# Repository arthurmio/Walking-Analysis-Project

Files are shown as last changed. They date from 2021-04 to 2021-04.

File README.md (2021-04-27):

# Walking-Analysis-Project
Projet d'analyse de la marche réalisé par :
  - GOURDON Mathéo
  - MARIANO Arthur 
  - TRIGUI Ianis

Ce projet a été développé dans le cadre du projet "Fil Rouge" en 5ème année à l'ESIEE Paris.  
Ce prototype d'analyse propose une solution d'analyse de la marche sans fil à l'aide d'Arduinos 33 BLE et de capteurs inertiels (BNO005) connectées grâce au protocole BLE (Bluetooth Low Energy). La lecture et l'interprétation des données sont réalisées à l'aide d'une interface sous Python.

# How to use it
Afin d'utiliser correctement le prototype veuillez vous référer à la notice d'utilisation dans le répertoire "Documentation".

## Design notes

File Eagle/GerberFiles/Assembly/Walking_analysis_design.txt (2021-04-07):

Partlist exported from C:/Users/Mathéo/Desktop/ESIEE/E5FE/projet_marche/Walking_analysis_design.sch at 14/03/2021 18:37

Qty Value               Device               Package              Parts Description                                      DESCRIPTION                                      HEIGHT MANUFACTURER_NAME MANUFACTURER_PART_NUMBER POPULARITY PROD_ID    RS_PART_NUMBER RS_PRICE-STOCK                                  VALUE
1                       RESISTORAXIAL-0.3    AXIAL-0.3            R1    Generic Resistor Package                                                                                                                                                                                                                      
1   0.1uF               0.1UF-KIT-EZ-50V-20% CAP-PTH-SMALL-KIT    C1    0.1µF ceramic capacitors                                                                                                                                       CAP-08370                                                                 0.1uF
1   5MS3S402AM2QES      5MS3S402AM2QES       5MS3S402AM2QES       S1    PCB Slide Switch SPDT On-Off-On 5 A@ 28 V dc Top PCB Slide Switch SPDT On-Off-On 5 A@ 28 V dc Top 9.91mm RS Components     5MS3S402AM2QES                                 7347334        https://uk.rs-online.com/web/p/products/7347334      
1   ARDUINO-NANO-3.0    ARDUINO-NANO-3.0     ARDUINO-NANO-3.0     M1    Arduino Nano 3.0 and compatible devices                                                                                                                                                                                                       
1   BNO055              BNO055               BNO055_FOOTPRINT     U$1   BNO055_walking analysis                                                                                                                                                                                                                       
1   POWER_JACKPTH_BREAD POWER_JACKPTH_BREAD  POWER_JACK_PTH_BREAD J1    Power Jack Connector                                                                                                                                           COMP-13253                                                                     
1   SFH482              SFH482               SFH482               D1    IR LED                                                                                                                                              0

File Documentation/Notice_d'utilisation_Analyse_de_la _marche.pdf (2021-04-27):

# Notice d’utilisation Prototype d’analyse de la marche sans fil

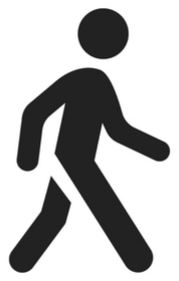
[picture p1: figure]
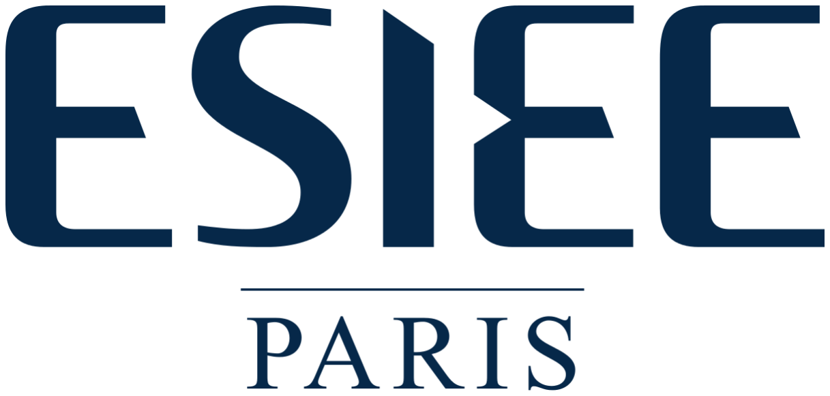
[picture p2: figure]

GOURDON Mathéo
MARIANO Arthur
TRIGUI Ianis

E5FE
2020 - 2021

# Table des matières

Introduction | 3
Matériel nécessaire | 3
Comment utiliser le dispositif | 4
Téléversement des programmes Arduino | 5
Utilisation de l’interface Python | 6

# Introduction

Ce document a pour objectif d’être une notice d’utilisation du projet Analyse de la marche réalisé dans le cadre du projet fil rouge à l’ESIEE Paris. Tous les fichiers nécessaires sont disponibles sur notre github (https://github.com/arthurmio/Walking-Analysis-Project).

Notre document est séparé en deux grandes parties :
- Hardware : consistant en le matériel nécessaire et comment l’utiliser
- Software : consistant à téléverser les programmes Arduino et à utiliser l’interface Python

Pour toutes questions liées à l’utilisation ou à la compréhension de certains fichiers, n’hésitez pas à contacter un des contributeurs du github.

# Matériel nécessaire

Pour se servir de notre dispositif, il est essentiel de se munir de tout le matériel nécessaire. Pour ce qui est du dispositif en lui-même il nous faudra donc les éléments suivant:
- 7 boîtiers;
- 7 batteries chargées 9V;
- 7 circuits imprimés;
- Un ordinateur;
- Un câble micro-usb -> USB.

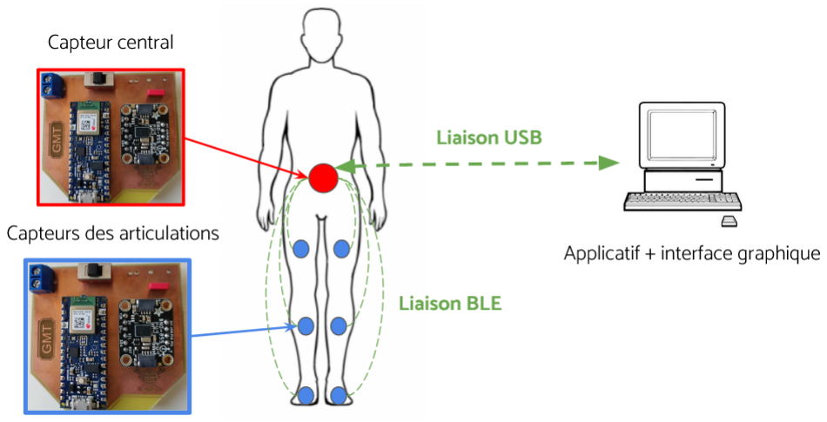
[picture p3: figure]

# Comment utiliser le dispositif

Pour installer le matériel il faut tout d’abord passer les languettes de scratch dans les boîtiers grâce à la fente prévue à cet effet. Puis brancher les batteries aux cartes imprimées de cette manière :

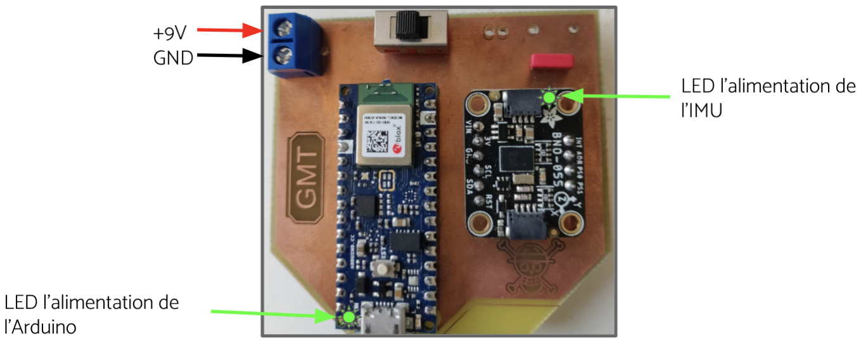
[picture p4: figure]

Si le système est correctement alimenté, alors les LEDs d’alimentation vertes seront allumées sur l’Arduino ainsi que sur le BNO055

Une fois chaque carte alimentée, il faut insérer les batteries dans le boîtier à l’intérieur des encoches afin de les maintenir. Une fois les batteries placées, nous pouvons ajouter le circuit imprimé dans le boîtier et le fermer. La carte reliée au dos doit être reliée grâce au câble micro-usb à un ordinateur portable.

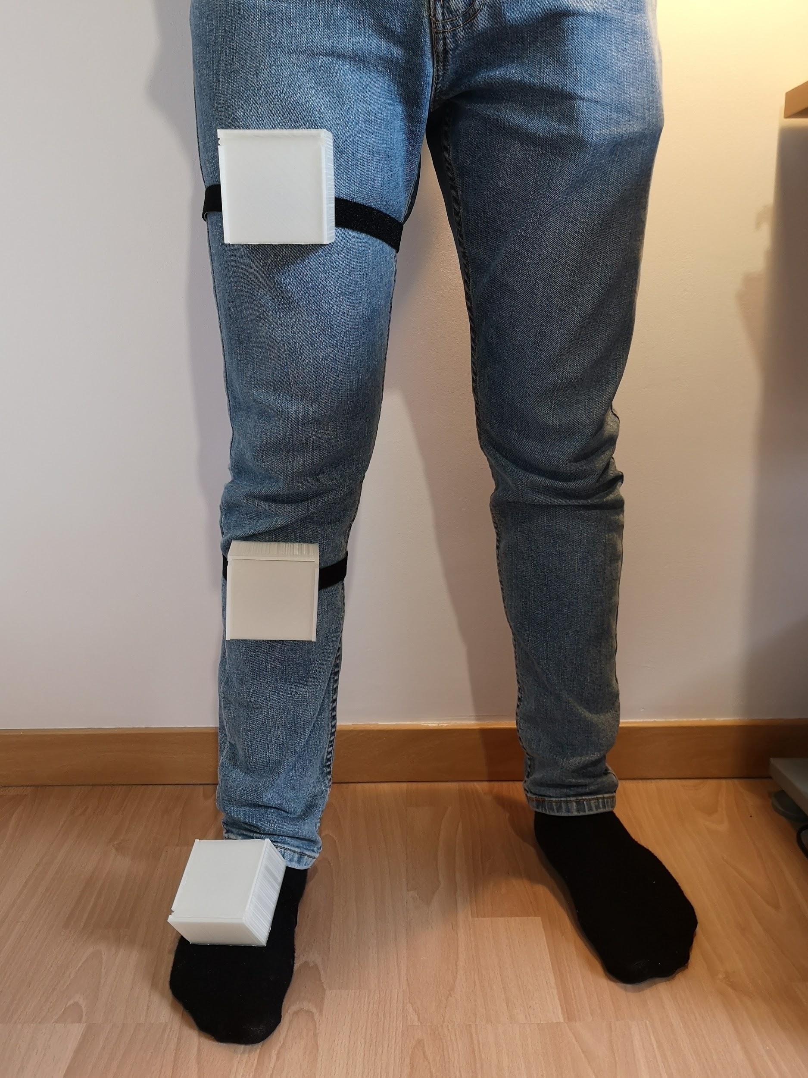
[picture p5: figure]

Pour mettre le circuit en route il suffit d’activer les interrupteurs de chaque carte.

# Téléversement des programmes Arduino

Le logiciel de développement utilisé pour les programmes des cartes Arduino est l’IDE Arduino. Il faudra donc tout d'abord installer l’environnement, pour installer les drivers et les librairies qui seront utilisés pour communiquer avec l’Arduino Nano 33 BLE ainsi qu’avec l’IMU BNO055.

Puis il faudra téléverser les programmes sur l’ensemble des cartes arduino.
Commençons par les 6 capteurs périphériques, les programmes sont situés dans l’arborescence suivante dans le Github : Walking-Analysis-Project/Arduino/Peripherals Chacunes des 6 Arduinos périphériques devront être téléversées avec un programme différent peu importe l’ordre. Les programmes sont notés Peripheral_X.ino avec X allant de 1 à 6. Une fois cette étape réalisée, les périphériques sont désormais initialisés.

Passons maintenant à la centrale, le programme se situe dans l’arborescence suivante : Walking-Analysis-Project/Arduino/Central et le programme se nomme Central.ino, il suffit de le téléverser sur la carte centrale.

Lorsque toutes les cartes auront reçu leur programme maintenant il faut réaliser une calibration rapide des IMUs, pour cela il suffit simplement de tenir dans sa main la capteur et de l’orienter dans toutes les directions.

Une fois toutes les étapes précédentes réalisées, le système est prêt à l’emploi. Afin de notifier si un périphérique se connecte à la centrale, il suffit de regarder si la LED orange est allumée ou non. Si le système fonctionne bien, la centrale devrait se connecter puis se déconnecter à l’ensemble des périphériques. A noter qu’une connexion dure moins d’une seconde.

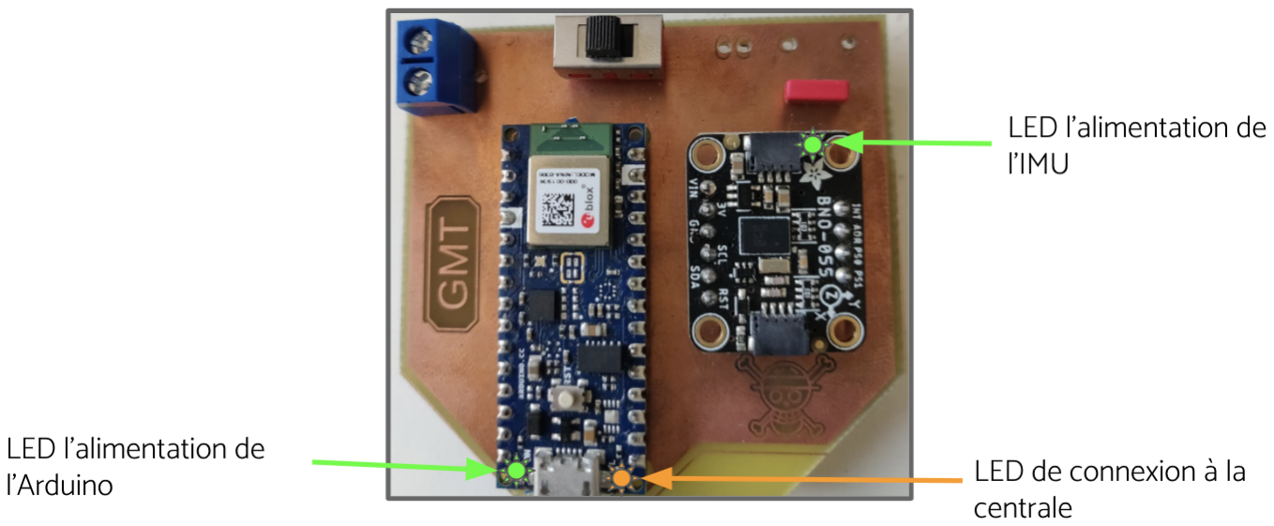
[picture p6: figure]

Si jamais le système cesse de fonctionner, il suffit de re-téléverser le code de la centrale ou bien de “reset” les périphériques bloqués en connexion en appuyant 2 fois sur le bouton reset de l’Arduino concernée.

# Utilisation de l’interface Python

Notre interface à été réalisé sur Python (version 3.9.2). L’IDE de développement a été Visual Studio Code mais ce n’est absolument pas une nécessité de l’utiliser pour faire fonctionner ces programmes.

Cette interface utilise différentes librairies qui devront être téléchargés pour pouvoir exécuter le programme (voir en-tête de chaque programme) :
- numpy;
- matplotlib;
- time;
- serial;
- tkinter.

Les fichiers d’interface sont situés dans le répertoire “python” du github.
Il existe 4 fichiers différents avec chacune une particularité (décrite dans l’en-tête en commentaire) :
- interface.py : est un fichier d’interface (de l’arduino) réalisé avec tkinter permettant de lisser les courbes (peut poser problème);
- interface_bis.py : est le même fichier que interface.py, cependant sans le lissage des courbes (à utiliser principalement);
- serie.py : qui est notre interface avec un affichage des courbes en temps réel (fonctionne moyennement car beaucoup de données sont compliquées à être affichées);
- data_save.py : affiche les différentes courbes de l’arduino, cependant sans l’interface créée avec tkinter.

Avant l’exécution d’un de ces 4 programmes, il faut préciser sur quel port COM est connectée notre arduino centrale.
Pour paramétrer le port COM que nous utilisons dans le programme, il faut modifier la ligne suivante : arduinoData=serial.Serial('COM4', 115200).

Une fois les librairies et les fichiers téléchargés, le port COM paramétré, vous pouvez exécuter un des 4 fichiers en utilisant python3.

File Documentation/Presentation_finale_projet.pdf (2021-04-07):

Projet fil rouge
Présentation finale projet Mme Abir Rezgui

# Analyse de la marche

Mathéo Gourdon
Arthur Mariano
Ianis Trigui

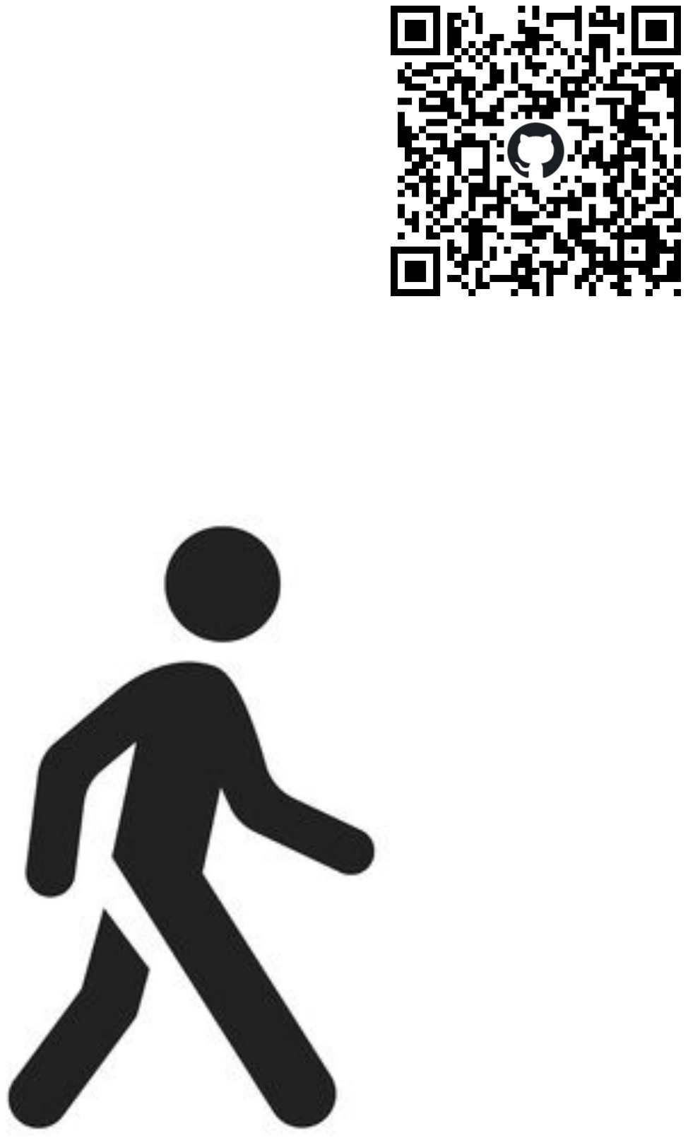
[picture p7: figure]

06/04/2021 | 1

## matières

## Table des

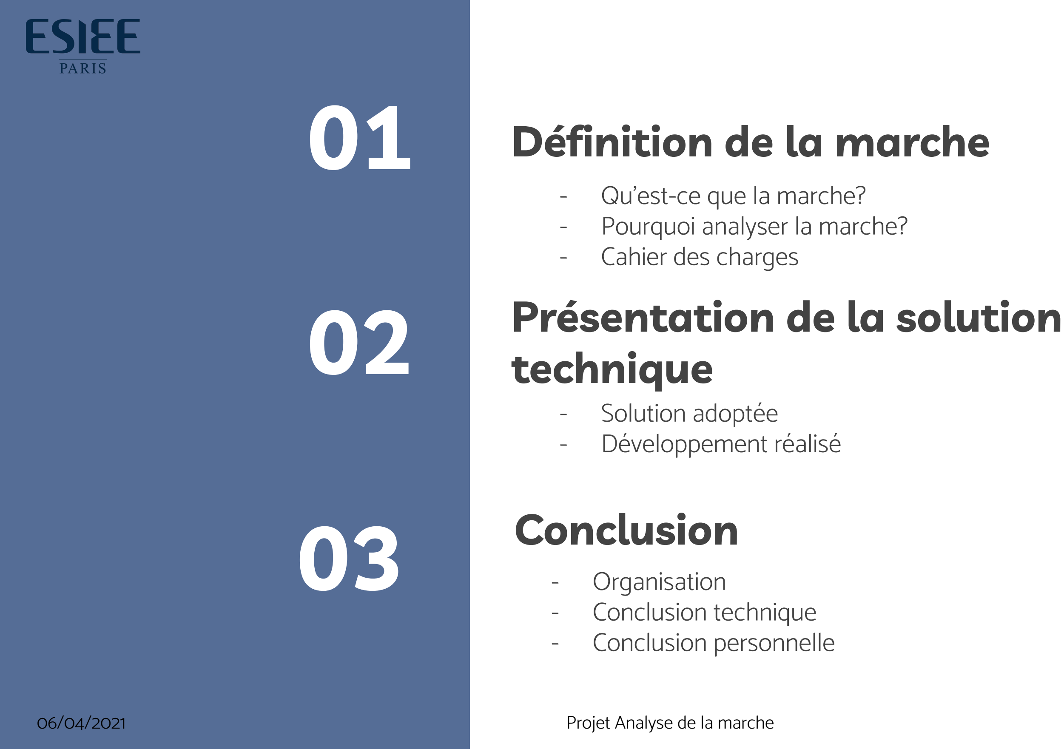
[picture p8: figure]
Conclusion 03; 01 Définition de la marche; Présentation de la solution; Projet Analyse de la marche

technique - Solution adoptée - Développement réalisé

- Qu’est-ce que la marche? - Pourquoi analyser la marche? - Cahier des charges
- Organisation - Conclusion technique - Conclusion personnelle

Projet Analyse de la marche

# 01 - Introduction

## a) Qu’est-ce que la marche?

## b) Pourquoi analyser la marche?

## c) Cahier des charges

06/04/2021 | 3

## Définition de la marche

Projet Analyse de la marche | 4

La marche peut être définie comme un déplacement consistant en une translation de l’ensemble du corps, consécutive à des mouvements de rotations articulaires.

Elle utilise une répétition de séquences des segments corporels pour déplacer le corps vers l’avant en maintenant l’équilibre.

Bouisset et Maton, 1995

Perry, 1992

06/04/2021

## Définition de la marche

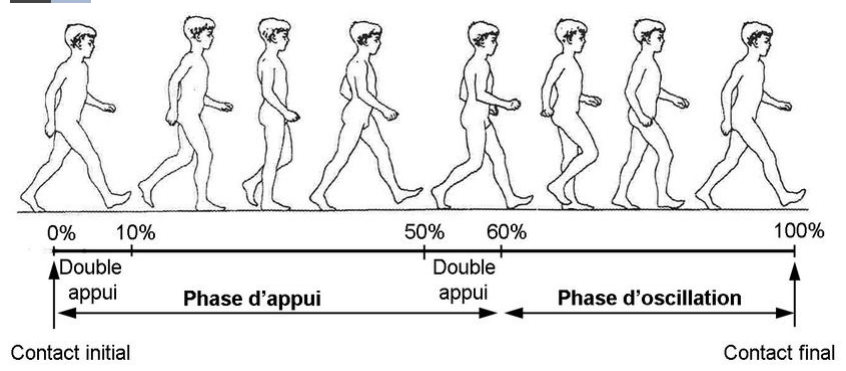
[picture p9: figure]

06/04/2021 | Projet Analyse de la marche | 5

Projet Analyse de la marche

# 01 - Introduction

## a) Qu’est-ce que la marche?

## b) Pourquoi analyser la marche?

## c) Cahier des charges

06/04/2021 | 6

## Pourquoi analyser la marche ?

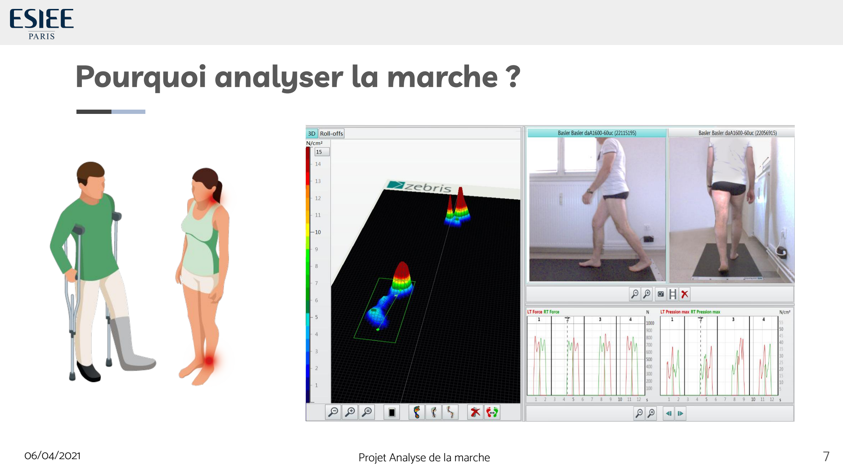
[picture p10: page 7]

06/04/2021 | Projet Analyse de la marche | 7

Projet Analyse de la marche

# 01 - Introduction

## a) Qu’est-ce que la marche?

## b) Pourquoi analyser la marche?

## c) Cahier des charges

06/04/2021 | 8

## Cahier des charges

06/04/2021 | Projet Analyse de la marche

Objectif du projet : Proposer une solution d’analyse de la marche sans fil à moindre coût
Besoins :
- Interconnexion de capteurs en Bluetooth et lire les données avec une fréquence d’acquisition de 100 Hz
- Réaliser une interface graphique permettant de lire les données reçues des différents capteurs
- Réaliser des PCB + un boîtier en modèle 3D pour rendre le dispositif utilisable

Projet Analyse de la marche

# 02 - Présentation de la solution technique

## a) Solution adoptée

## b) Développement réalisé

1) PCB + Impression 3D
2) Arduino
3) Interface Python
06/04/2021 | 10

## Schéma de connectivité de notre système

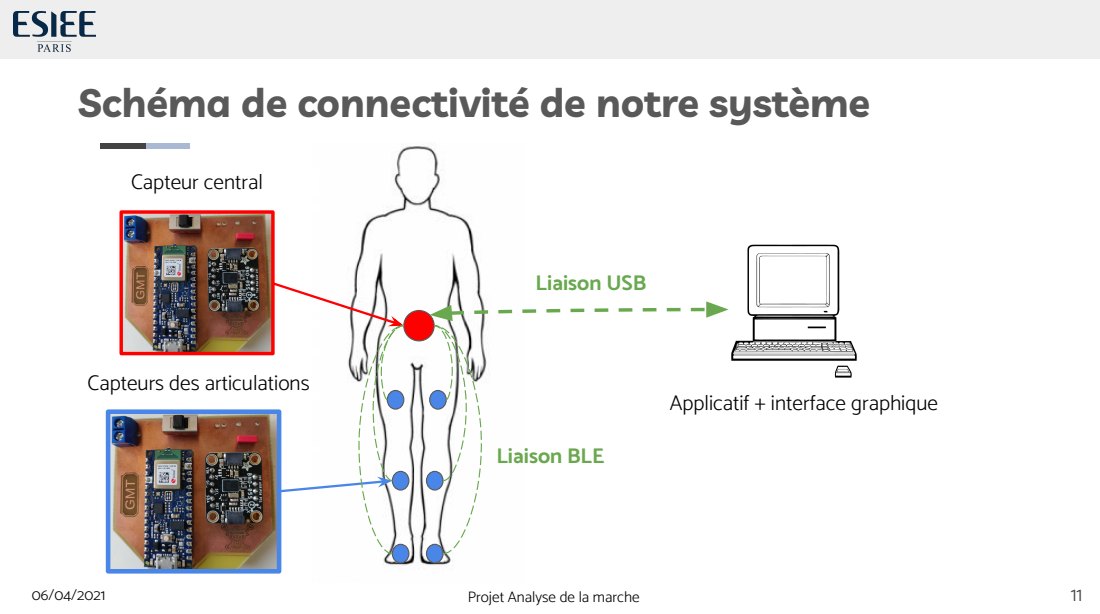
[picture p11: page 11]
Projet Analyse de la marche; Liaison BLE; Liaison USB; Capteur central

Capteurs des articulations

Applicatif + interface graphique

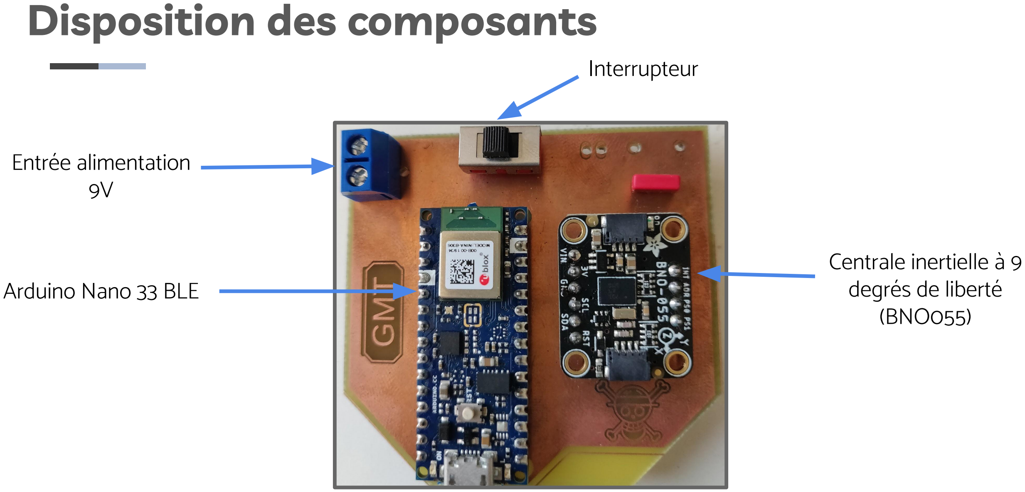
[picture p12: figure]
Disposition des composants; Entrée alimentation 9V; Interrupteur; Centrale inertielle à 9 degrés de liberté (BNO055); Arduino Nano 33 BLE

Projet Analyse de la marche

06/04/2021 | 12

Projet Analyse de la marche

# 02 - Présentation de la solution technique

06/04/2021 | 13

## a) Solution proposée

## b) Développement réalisé

1) PCB + Impression 3D
2) Arduino
3) Interface Python

## Réalisation du PCB

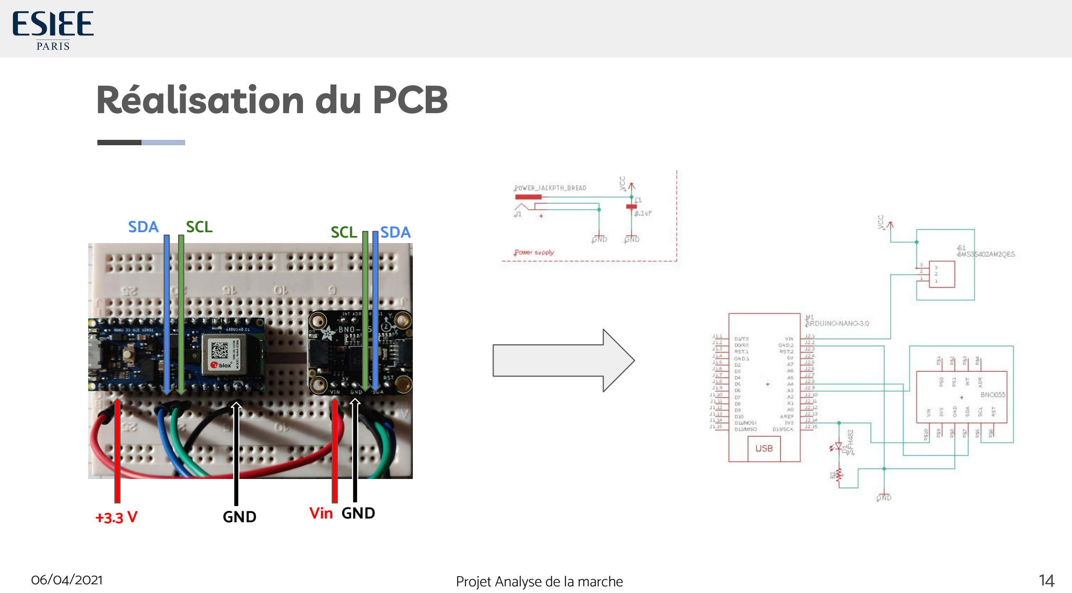
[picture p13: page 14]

SDA | | SCL
SCL | SDA
+3.3 V | GND | Vin GND
06/04/2021 | Projet Analyse de la marche | 14

## Réalisation du PCB

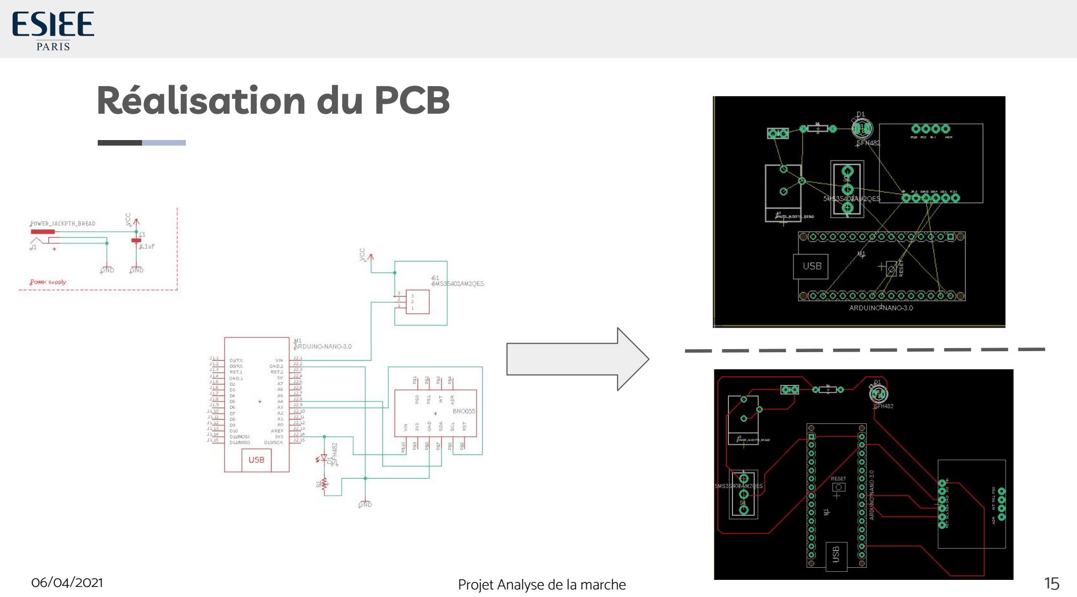
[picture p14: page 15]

06/04/2021 | Projet Analyse de la marche

## Réalisation du PCB

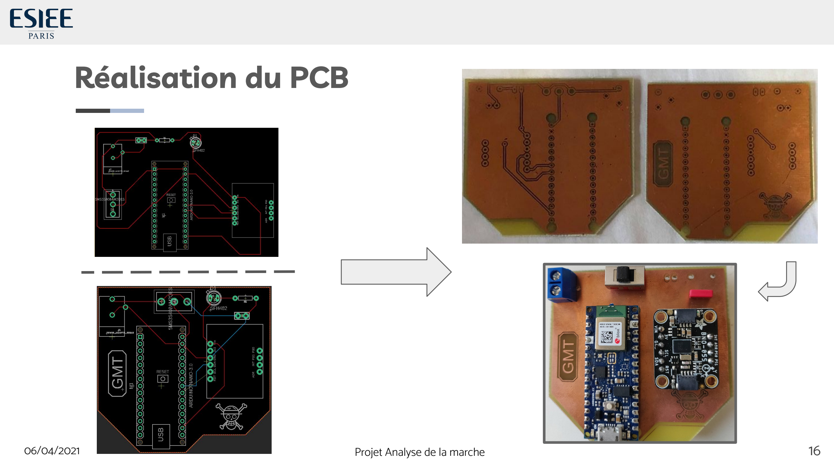
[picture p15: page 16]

06/04/2021 | Projet Analyse de la marche

## Conception du boîtier

- Mesure des dimensions des
différents composants
- Croquis du boîtier
- Création du modèle sur
SketchUp

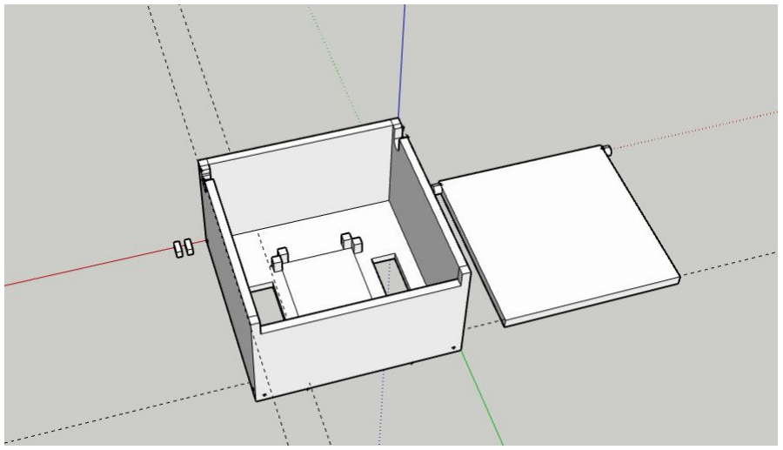
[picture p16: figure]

06/04/2021 | Projet Analyse de la marche | 17

## Conception du boîtier

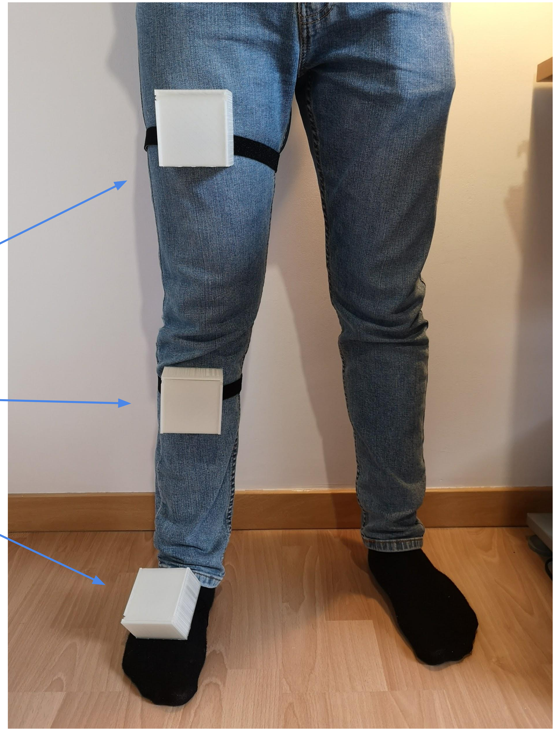
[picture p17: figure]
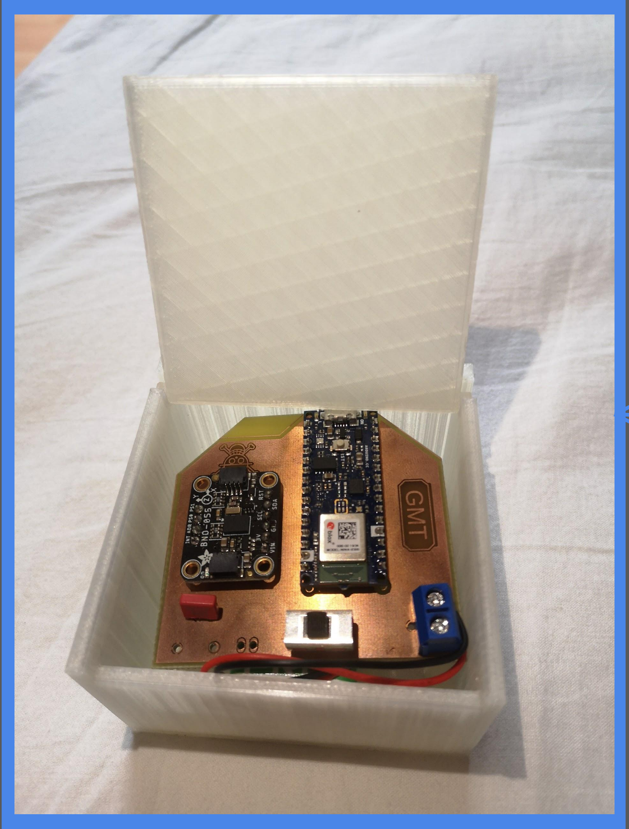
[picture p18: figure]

06/04/2021 | Projet Analyse de la marche

Projet Analyse de la marche

# 02 - Présentation de la solution technique

06/04/2021 | 19

## a) Solution adoptée

## b) Développement réalisé

1) PCB + Impression 3D
2) Arduino
3) Interface Python

## Travail réalisé sur les segments

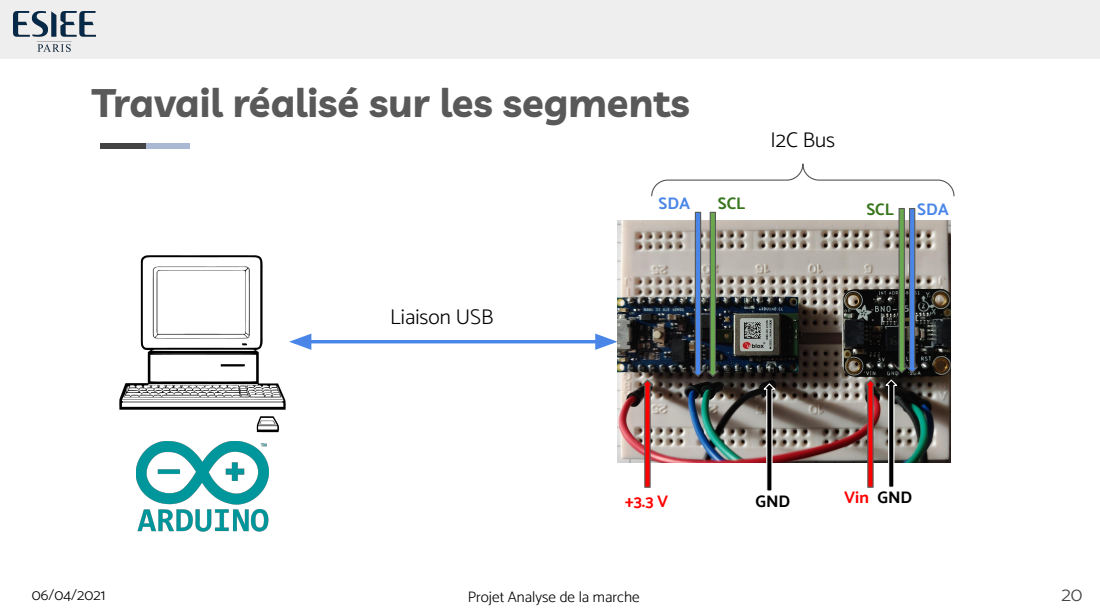
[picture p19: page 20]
Projet Analyse de la marche; GND; Vin GND; I2C Bus; Liaison USB

SDA | | SCL

SCL | SDA

## Choix des angles d’Euler

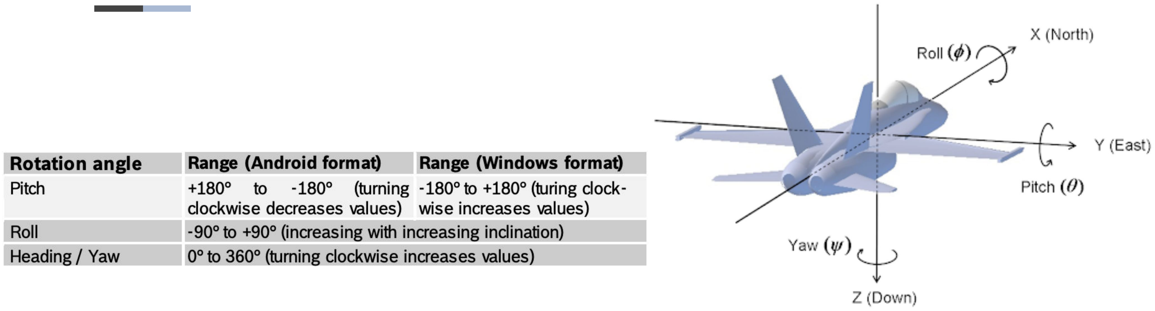
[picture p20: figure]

06/04/2021 | Projet Analyse de la marche | 21

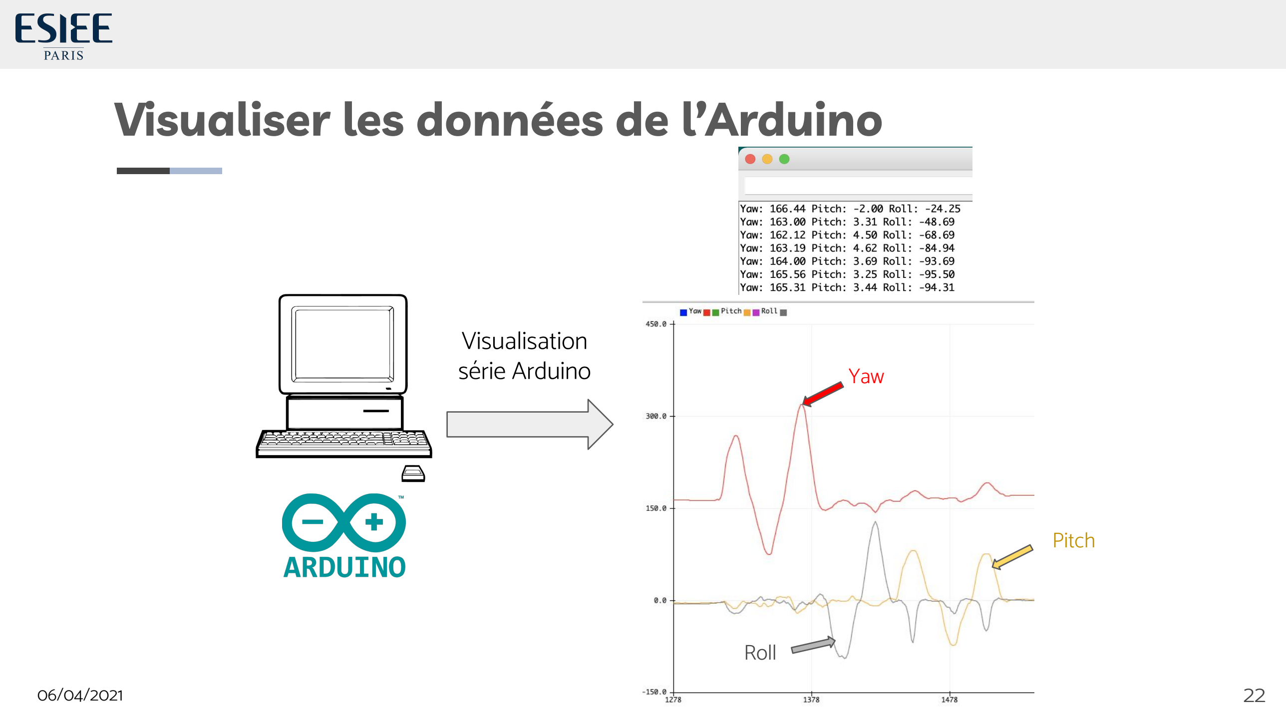
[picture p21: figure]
Visualiser les données de l’Arduino; Yaw; Pitch; Roll; Visualisation série Arduino

## Fonctionnement du BLE (Bluetooth Low Energy)

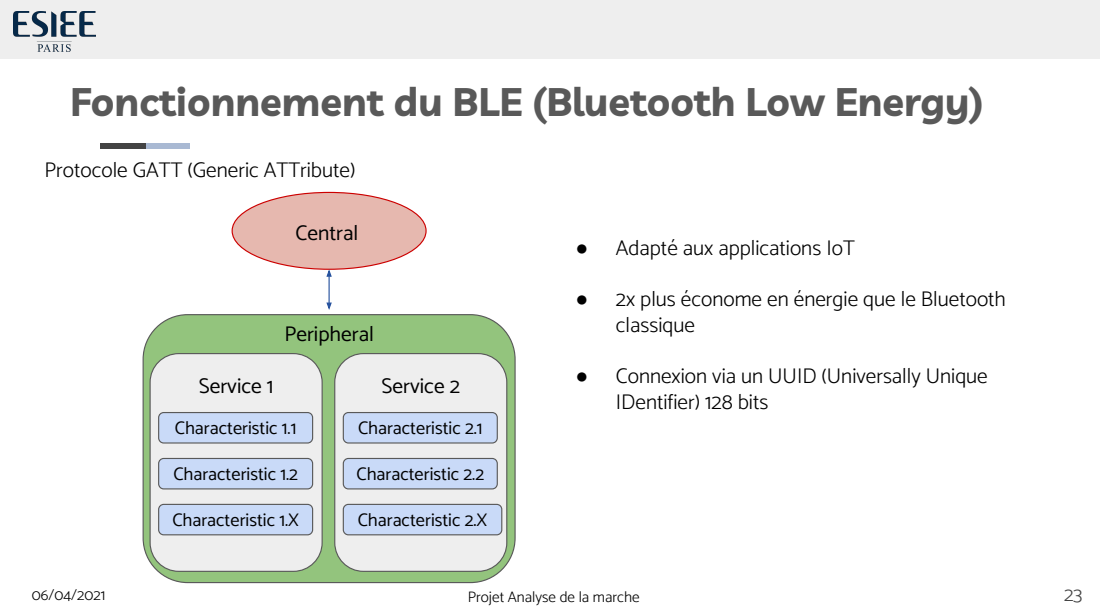
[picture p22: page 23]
Service 1; Characteristic 1.1; Characteristic 1.2; Characteristic 1.X; Service 2; Characteristic 2.1; Characteristic 2.2; Characteristic 2.X; Central; Peripheral

Protocole GATT (Generic ATTribute)

● Adapté aux applications IoT
● 2x plus économe en énergie que le Bluetooth
classique
● Connexion via un UUID (Universally Unique
IDentifier) 128 bits

Projet Analyse de la marche

## Envoyer les données par BLE

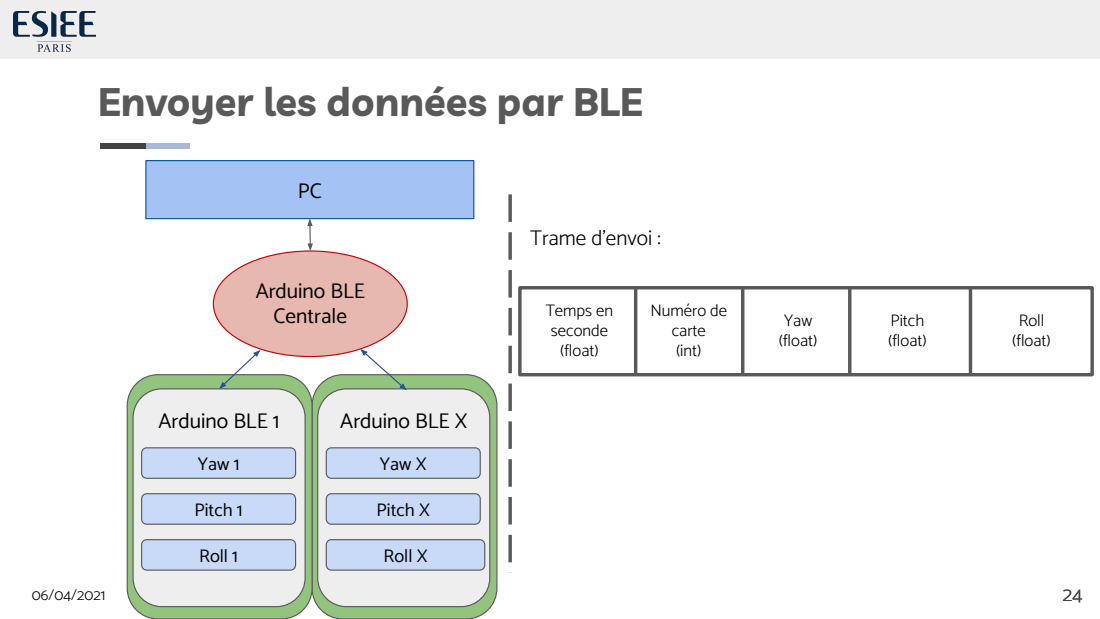
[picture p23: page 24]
Arduino BLE 1; Yaw 1; Pitch 1; Roll 1; Arduino BLE X; Yaw X; Pitch X; Roll X; Arduino BLE Centrale; Temps en seconde (float); Numéro de carte (int); Yaw (float); Pitch (float); Roll (float); Trame d’envoi :

## Contraintes de l’Arduino avec la multi connexion BLE

- Hardware capacitaire jusqu’à une connexion simultanée de 8 périphériques
Problème : Librairies Arduino non-adaptées à la multi connexion
Solution : Etablir des connexions puis des déconnexions séquentielles avec chaque périphériques

Projet Analyse de la marche

| Multi connexion | Connexion séquentielle
Avantages | Fréquence d’acquisition élevée | Gestion/Connexion plus simple aux périphériques
Inconvénients | Difficile à mettre en place sur Arduino | Fréquence d’acquisition trop faible Connexions aléatoires

06/04/2021

Projet Analyse de la marche

# 02 - Présentation de la solution technique

06/04/2021 | 26

## a) Solution proposée

## b) Développement réalisé

1) PCB + Impression 3D
2) Arduino
3) Interface Python

## Interface python

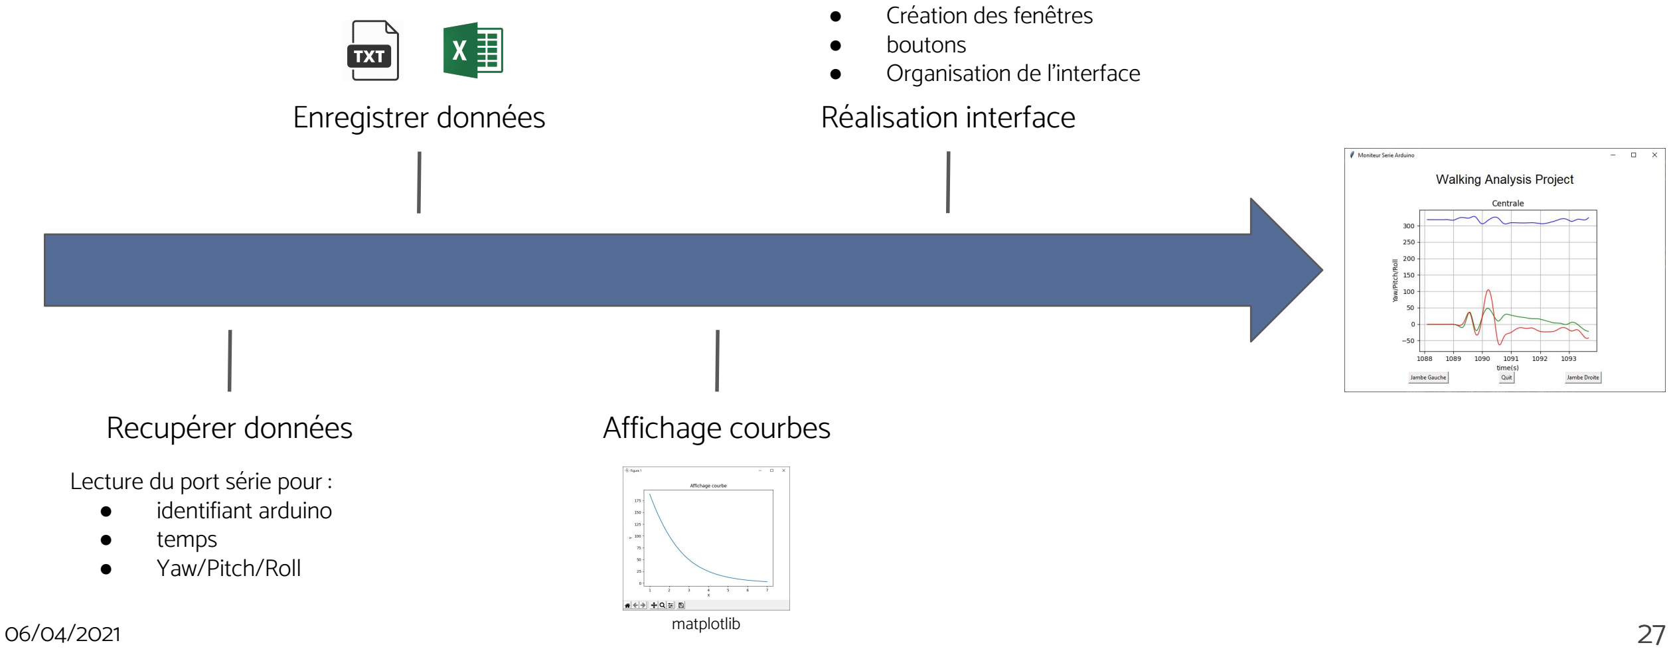
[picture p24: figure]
Recupérer données; Enregistrer données; Affichage courbes; Réalisation interface; Lecture du port série pour : ● identifiant arduino ● temps ● Yaw/Pitch/Roll; matplotlib; ● Création des fenêtres ● boutons ● Organisation de l’interface

Interface python; Interface réalisée avec Tkinter; Affichage segments jambe droite; Affichage segments jambe gauche; Insertion graphe réalisé avec matplotlib; Yaw Pitch Roll

06/04/2021 | Projet Analyse de la marche | 28

## Interface python

06/04/2021 | Projet Analyse de la marche

Projet Analyse de la marche

# Conclusion

## a) Organisation

## b) Conclusion technique

## c) Conclusion personnelle

06/04/2021 | 30

## Diagramme de Gantt


06/04/2021 | Projet Analyse de la marche | 31

6 Avril 2021

Projet Analyse de la marche

# Conclusion

## a) Organisation

## b) Conclusion technique

## c) Conclusion personnelle

06/04/2021 | 32

## Réponse au cahier des charges

06/04/2021 | Projet Analyse de la marche

Objectif du projet : Proposer une solution d’analyse de la marche sans fil

Solution apportée :
- Connexion BLE avec cartes Arduino
- Lecture des segments sur une interface Python
- Réalisation des PCB + boîtier en modèle 3D

## Problèmes rencontrés

06/04/2021 | Projet Analyse de la marche


Problèmes software:
- Connexion carte STM
- Multi-connexion Bluetooth Arduino
- Environnement développement Python Problèmes hardware:
- Déconnexion intempestive des cartes Arduino
- Erreur de PCB

## Optimisations possibles

06/04/2021 | Projet Analyse de la marche

### 4 optimisations

Fréquence d’acquisition

Connexion centrale au PC
en BLE

Ré-imprimer nouveaux
PCB

Interface temps réel

Projet Analyse de la marche

# Conclusion

## a) Organisation

## b) Conclusion technique

## c) Conclusion personnelle

06/04/2021 | 36

## Conclusion personnelle

06/04/2021 | Projet Analyse de la marche
- Développement de connaissances techniques (protocole sans fil, IMH python, PCB, Github…)
- Organisation d’un projet
- Communications en équipe
- Prise de conscience de la complexité d’un projet

## Merci de votre attention !


06/04/2021 | Projet Analyse de la marche | 38

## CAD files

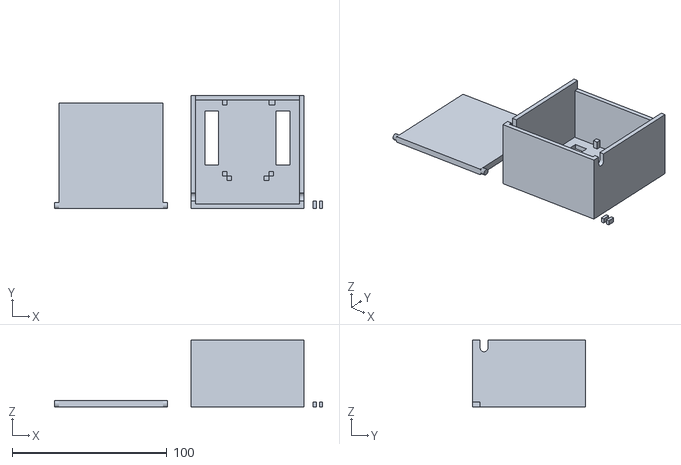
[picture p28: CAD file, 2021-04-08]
SketchUp/boitier.stl
173.0 x 73.0 x 43.0

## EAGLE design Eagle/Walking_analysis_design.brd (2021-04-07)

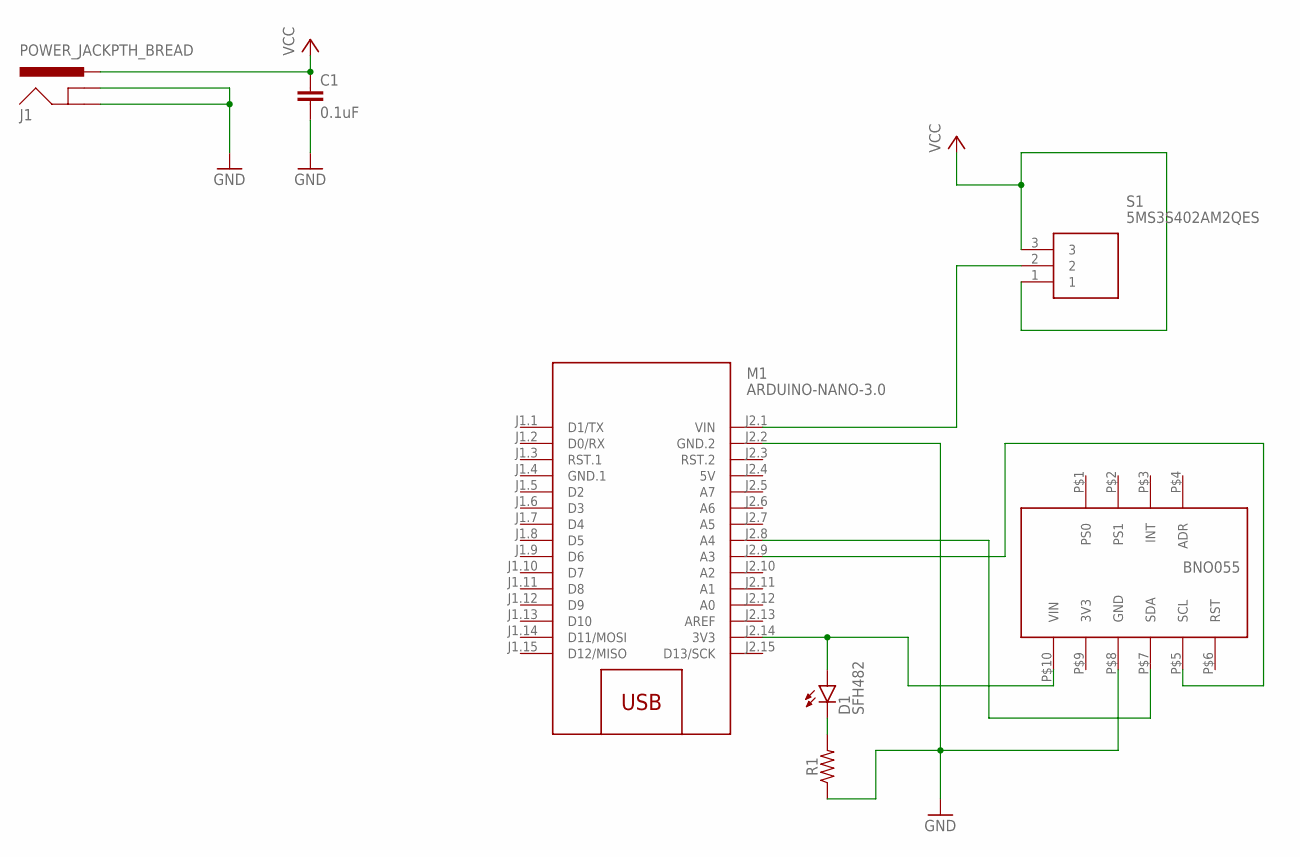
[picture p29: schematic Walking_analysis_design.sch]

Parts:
C1: 0.1uF; CAP-PTH-SMALL-KIT
D1: SFH482
J1: POWER_JACKPTH_BREAD; POWER_JACK_PTH_BREAD
M1: ARDUINO-NANO-3.0
R1: AXIAL-0.3
S1: 5MS3S402AM2QES
U$1: BNO055; BNO055_FOOTPRINT

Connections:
3V3: U$1.P$9 (3V3)
5V: M1.J2.4 (5V)
GND: C1.2, J1.GND, J1.GNDBREAK, M1.J2.2 (GND.2), R1.P$1 (1), U$1.P$8 (GND)
GND.1: M1.J1.4 (GND.1)
unnamed: M1.J2.8 (A4), U$1.P$7 (SDA)
unnamed: M1.J2.9 (A3), U$1.P$5 (SCL)
unnamed: D1.A, M1.J2.14 (3V3), U$1.P$10 (VIN)
unnamed: M1.J2.1 (VIN), S1.2
unnamed: D1.K (C), R1.P$2 (2)
VCC: C1.1, J1.PWR, S1.1, S1.3

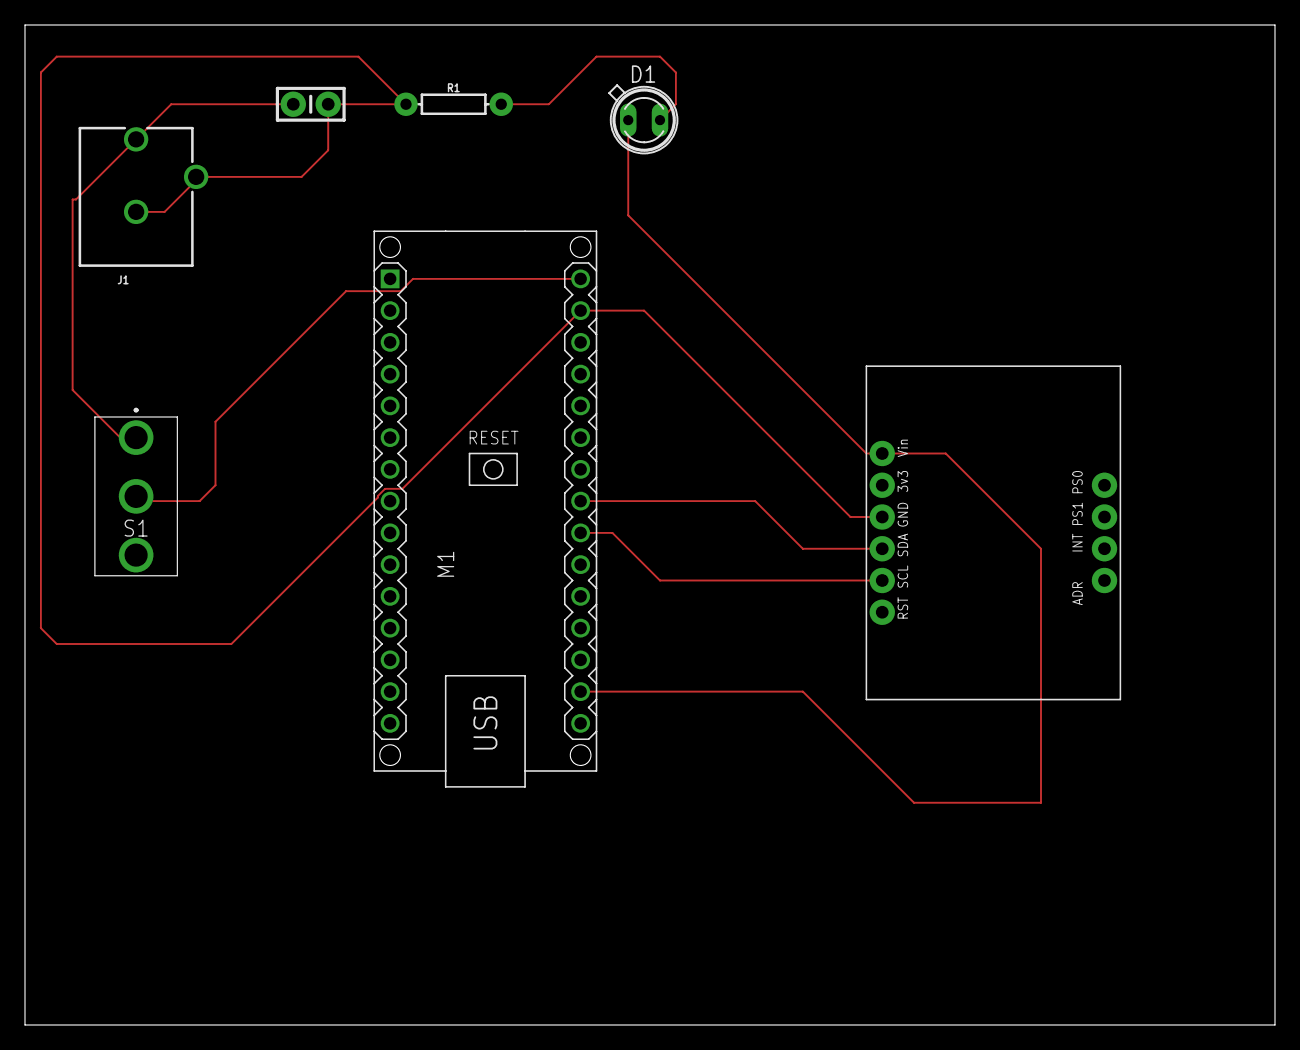
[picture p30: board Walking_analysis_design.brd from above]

Board: 2 copper layers, 100.0 x 80.0 mm, 7 parts (0 on the bottom side), 7 nets.

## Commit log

2021-01-19 Creation of Arduino and Python repository
2021-03-19 Arduino BLE connection
2021-03-24 Arduino data connected to python
2021-03-31 Data save + plot for all arduino
2021-04-06 Final Arduino files
2021-04-07 Files for PCB design with Eagle
    [Walking_analysis_design.brd, Walking_analysis_design.sch, copper_bottom.gbr, copper_top.gbr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]
2021-04-08 3D printing file of the case
    [boitier.stl]
2021-04-11 Rapport analyse de la marche

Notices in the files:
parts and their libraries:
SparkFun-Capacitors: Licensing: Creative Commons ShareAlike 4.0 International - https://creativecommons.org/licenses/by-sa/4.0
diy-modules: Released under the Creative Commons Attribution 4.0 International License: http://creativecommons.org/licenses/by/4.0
